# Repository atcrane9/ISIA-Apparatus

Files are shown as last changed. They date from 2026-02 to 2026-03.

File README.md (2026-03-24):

# ISIA-Apparatus

The "Immersive Social Interactions Assay" (ISIA) apparatus is a modular system designed to connect multiple mouse cages together, while allowing the option to restrict certain mice to specific cages.

The link to Methods Paper for this apparatus can be found [here]()

## Hardware

All files were printed using a Prusa i3 MKS3, using OVERTURE PLA Plus (PLA+) 1.75mm Professional Toughness filament.\
Painter's tape was put on print bed to increase print adhesion with bed.
* Make sure tape is completely flat
* No gaps between tape pieces
* If tape tears when removing print, replace with new piece
  
Nozzles used were either 0.4mm or 0.6mm, depending on specific part (Instructions for changing the nozzles [here](https://help.prusa3d.com/article/changing-or-replacing-the-nozzle-mk2-5-s-mk3-s-mk3-5-s_2069))
* **<ins>Must</ins>** be printed using **<ins>0.4mm nozzle</ins>**
  * [Cap](STL_Files/ISIA_Cap.stl)
  * [Adapter](STL_Files/ISIA_Adapter.stl)
  * [Inner Gate](STL_Files/ISIA_Inner_Gate.stl)
  * [Outer Gate](STL_Files/ISIA_Outer_Gate.stl)

_Note: These 4 parts contain threads that allow them to screw together. However, the threads must be "broken in" after printing, which is done by repeatedly screwing/unscrewing the parts with each other until they can easily twist the full range with minimal friction._

* Can be printed using **<ins>0.6mm nozzle</ins>**
  * [Tube](STL_Files/ISIA_Tube.stl)
  * [Restrictor](STL_Files/ISIA_Restrictor.stl)

### Cleaning
To clean the ISIA parts for reuse between experiments, scrub all surfaces vigorously using a sponge and dish soap.
* For the Tube, instead put dish soap on a toothbrush and scrub the inside and outside surfaces vigorously

_Note: While all other parts are reusable between experiments after cleaning, the Restictors are not resuasble, as the restricted mice often slightly chew on them in an attempt to reach the other cage. We advise printing new Restrictors for each experiment, and disposing of them when the experiment ends._

## Software

All parts sliced (aka rendered) using PrusaSlicer 2.9.2

Full print settings found here:\
[0.4mm nozzle settings](PrinterSettings/0.4nozzle_settings_no_support.ini)\
[0.6mm nozzle settings](PrinterSettings/0.6nozzle_settings_no_support.ini)

### Key Settings
* No skirt, no brim, no support material, no raft 
* First layer speed: 10mm/s 
* First layer height: 0.2mm 
* Infill density: 5%
* Layer Height:
  * For **<ins>0.4mm</ins>** Nozzle -> 0.3mm layer height
  * For **<ins>0.6mm</ins>** Nozzle -> 0.4mm layer height

# ISIA Apparatus Construction
_Note: See [Methods Paper]() for guide on how to modify mouse cages to work with this system_
1. Place Inner Gate on the inside of ISIA cage bottom, with the threads poking through the 51mm cage hole
   <p>
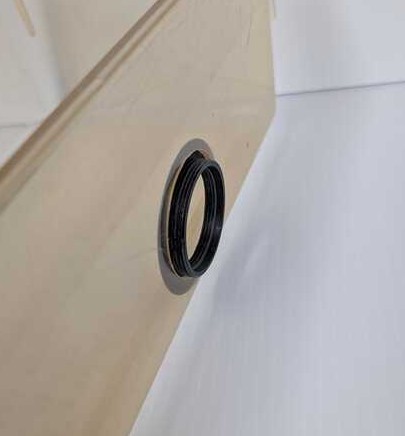
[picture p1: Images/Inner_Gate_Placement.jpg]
    
   </p>
2. Screw Outer Gate onto the threads of the Inner Gate
   * There are small ridges outside of the Outer Gates that go up ~3/4 of the height, leaving a small gap. This gap indicates the top of the Outer Gate, which is the side that screws onto the Inner Gate
   <p>
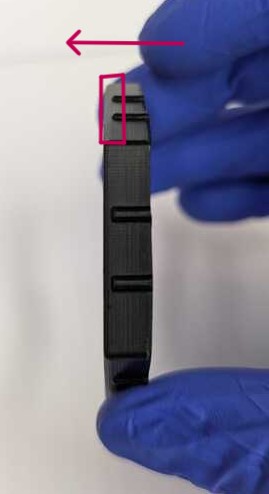
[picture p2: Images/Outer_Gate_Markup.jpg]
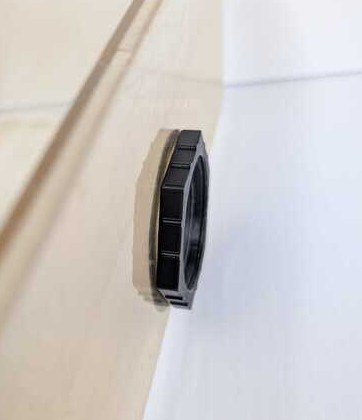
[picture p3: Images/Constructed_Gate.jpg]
     
   </p>
4. Repeat for both 51mm diameter cage holes

### To Close Gate:
* Screw Cap into Gate
  <p>
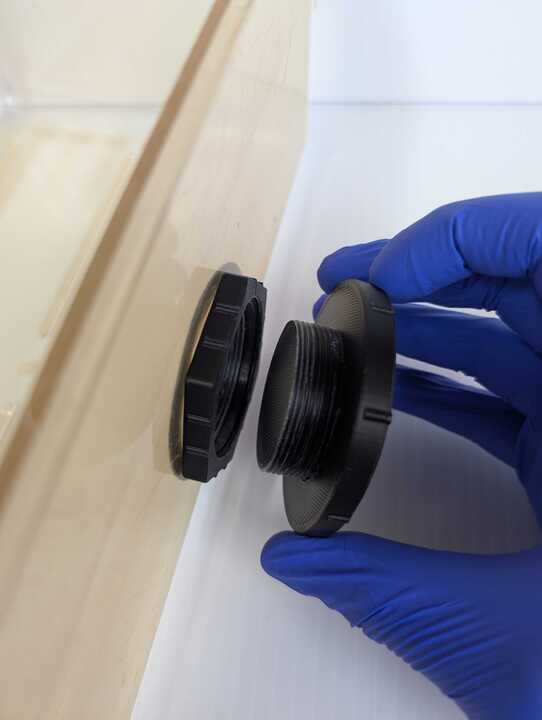
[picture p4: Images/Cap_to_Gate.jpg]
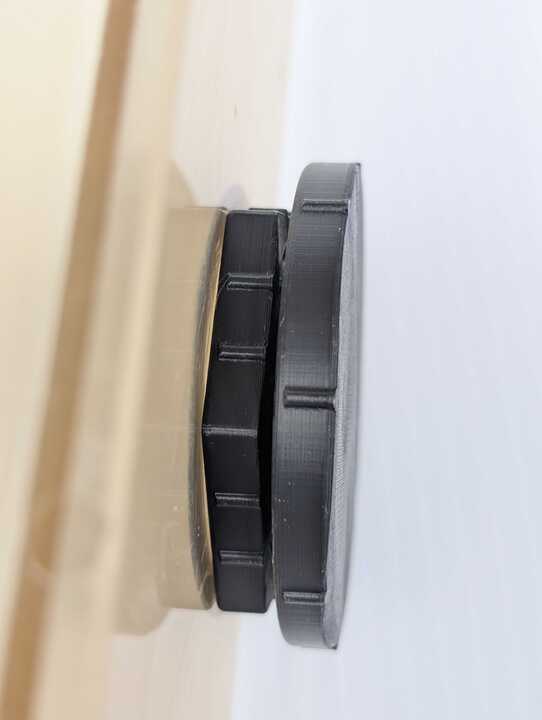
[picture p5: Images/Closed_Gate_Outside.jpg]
     
   </p>
  Should look like this from inside:
   <p>
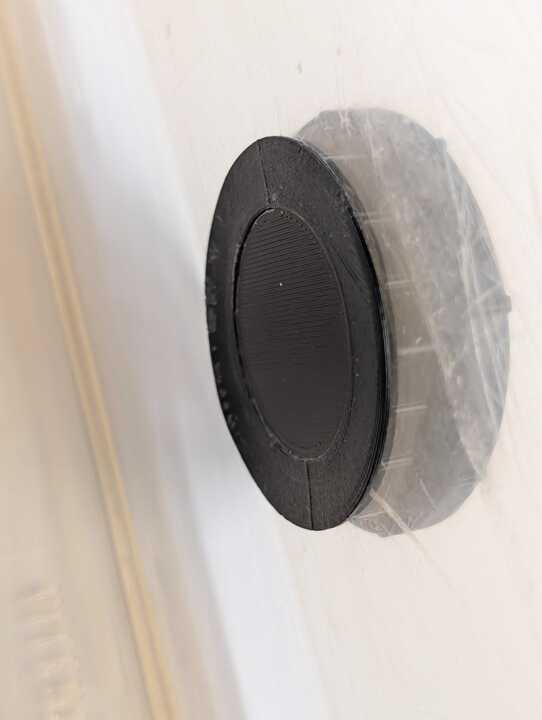
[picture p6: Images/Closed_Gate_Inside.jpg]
    
   </p>

### To Connect Gate to Tube:
* Screw Adapter into Gate
   <p>
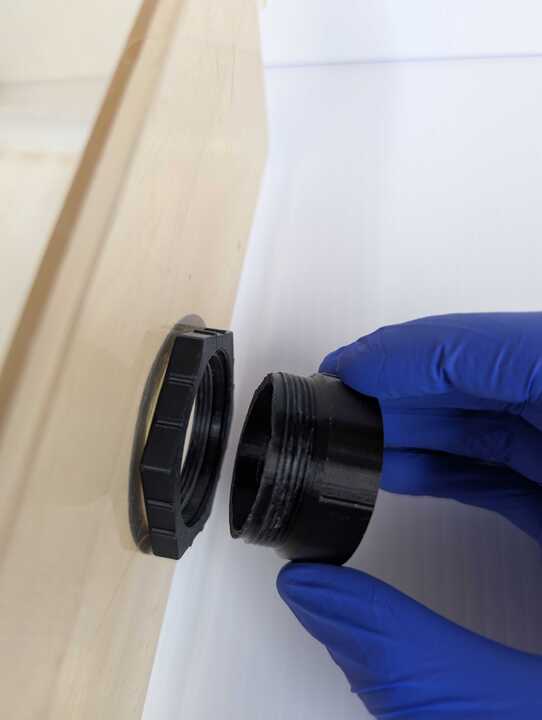
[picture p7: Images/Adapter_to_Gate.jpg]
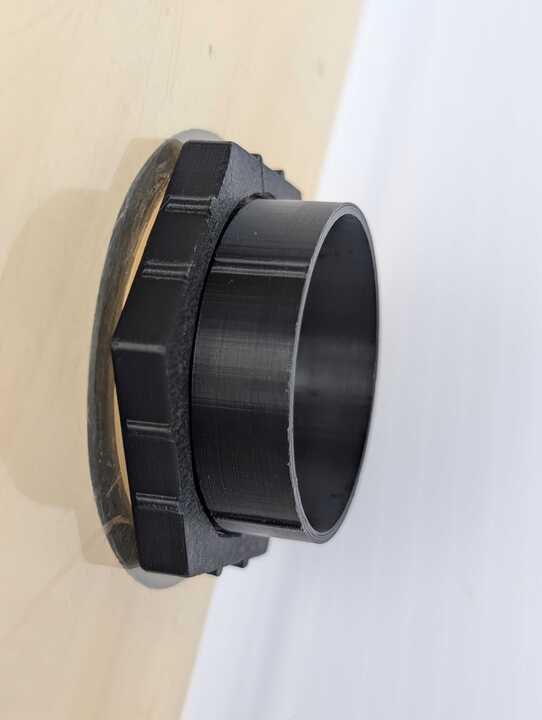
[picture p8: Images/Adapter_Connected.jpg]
     
   </p>
* Connect Tube to Adapter
  * _Note: The tube and adapter slide together, there is no screw with this connection_
  <p>
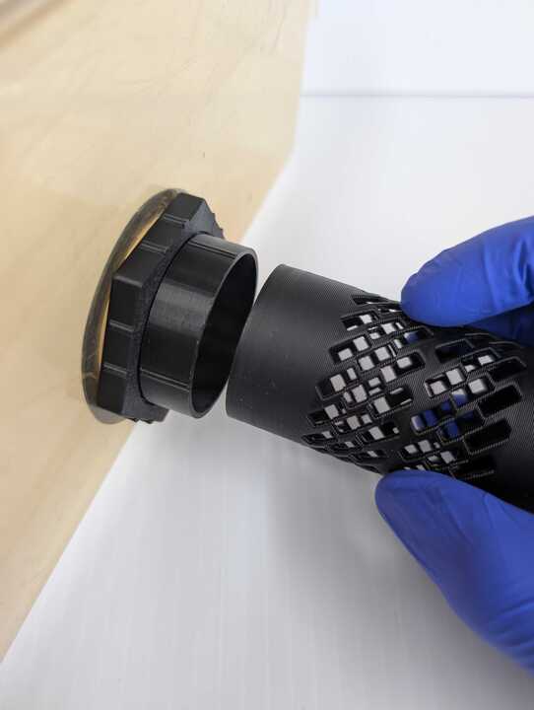
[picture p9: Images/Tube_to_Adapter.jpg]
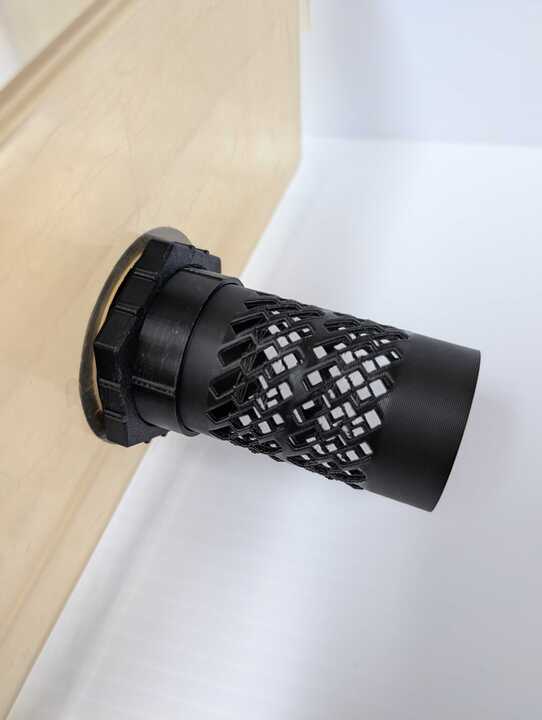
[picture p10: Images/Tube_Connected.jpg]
     
   </p>
* Connect second ISIA cage to other end of Tube
  * Make sure that water bottle holes are both facing the same direction
    * If they are opposite, swap the Cap and Adapter on one of the cages
  * Make sure to firmly push cages together to prevent tube from falling out
### To Restrict Mice
1. Separate cage containing restricted mouse from the tube
   <!-- * Can temporarily block open Gate with a Cap to prevent mice from escaping
     _Note that the Cap does not fit tightly into the Adapter, it is possible ????_
   <p>
    <img src=Images/Cap_to_Adapter.jpg height="290"> <img src=Images/Cap_block_Adapter.jpg height="290">
   </p> -->
2. Add Restrictor to exposed Tube entrance
   <p>
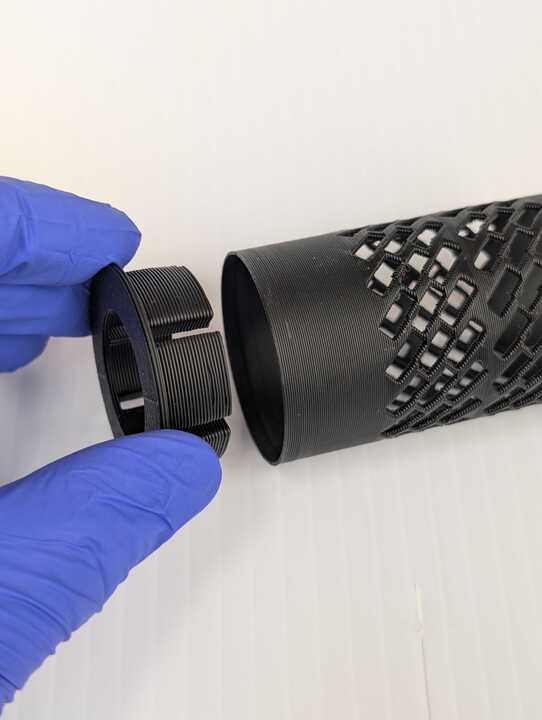
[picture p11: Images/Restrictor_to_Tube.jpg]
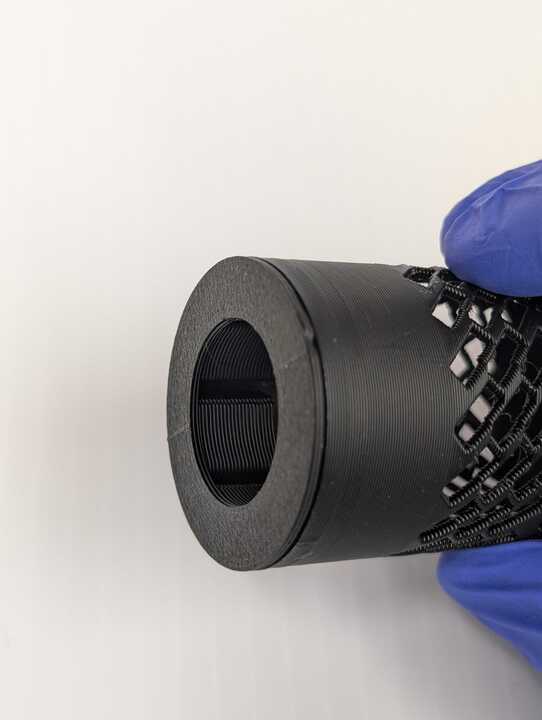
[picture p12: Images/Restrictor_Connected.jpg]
     
   </p>
3. Reconnect Tube to Adapter
   <p>
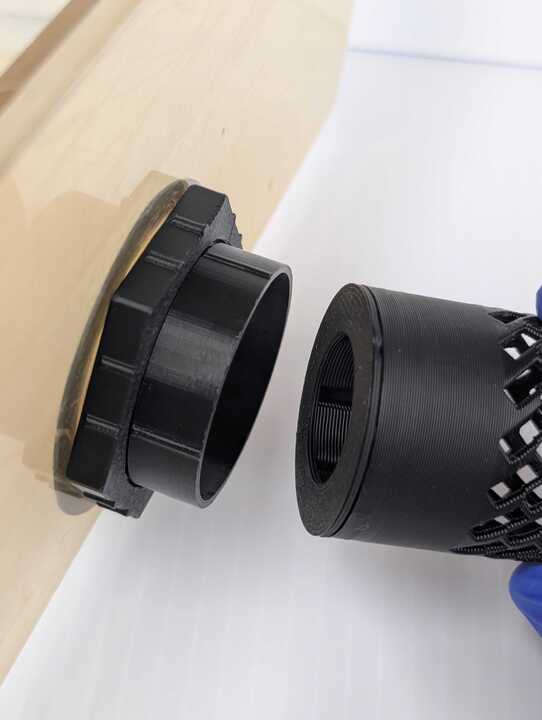
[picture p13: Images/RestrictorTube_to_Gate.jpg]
     
   </p>
   Should look like this from inside:<br/>
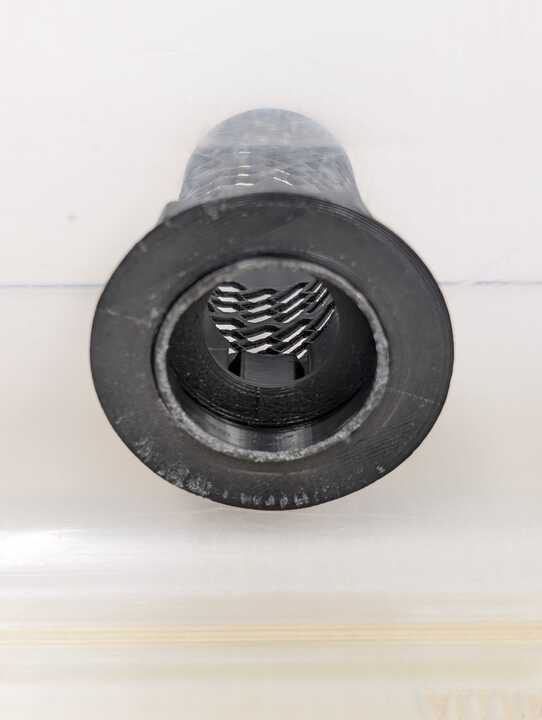
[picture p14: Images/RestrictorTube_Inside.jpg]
   

## Completed Setup looks like this:
   <p>
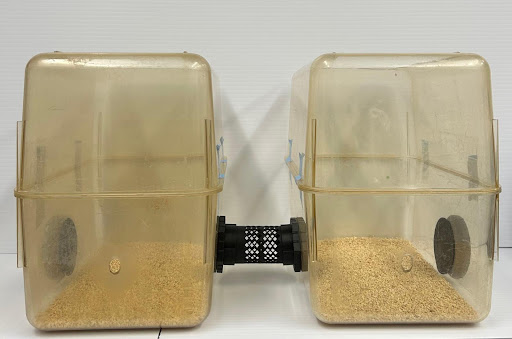
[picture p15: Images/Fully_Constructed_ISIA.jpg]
    
   </p>

# Acknowledgments

* [Aaron Crane](https://github.com/atcrane9) - Original designs for the Cap, Adapter, Inner and Outer Gates, updates to the Tube design, and compatibility of entire ensamble
* [The AER Lab](https://github.com/AER-Lab)
* [Matt Gaidica](https://github.com/mattgaidica) - First iteration design of Tube, Restrictor (Insert), and Flange

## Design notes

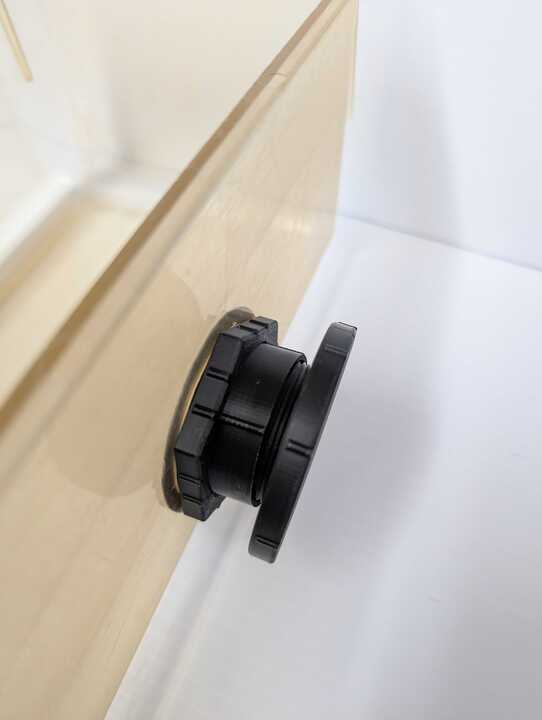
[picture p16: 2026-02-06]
Images/Cap_block_Adapter.jpg

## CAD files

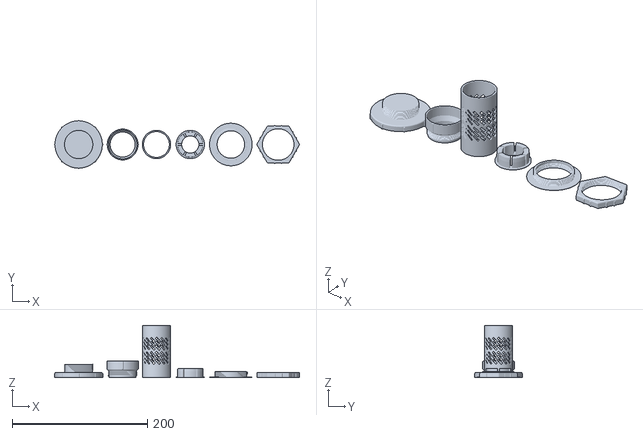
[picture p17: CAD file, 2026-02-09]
STL_Files/ISIA_Ensamble.stl
362.2 x 71.5 x 77.6

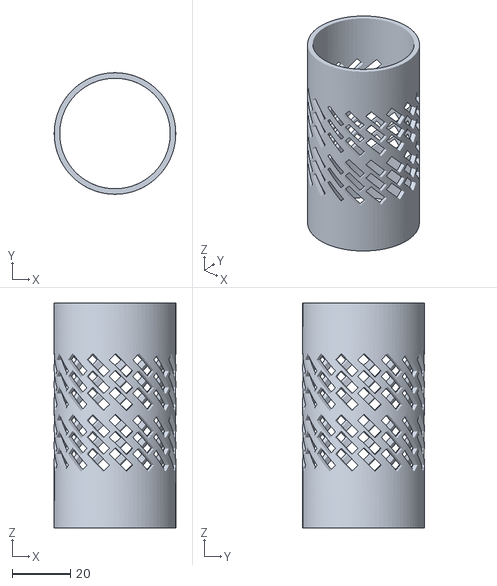
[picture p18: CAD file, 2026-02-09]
STL_Files/ISIA_Tube.stl
41.9 x 41.9 x 77.6

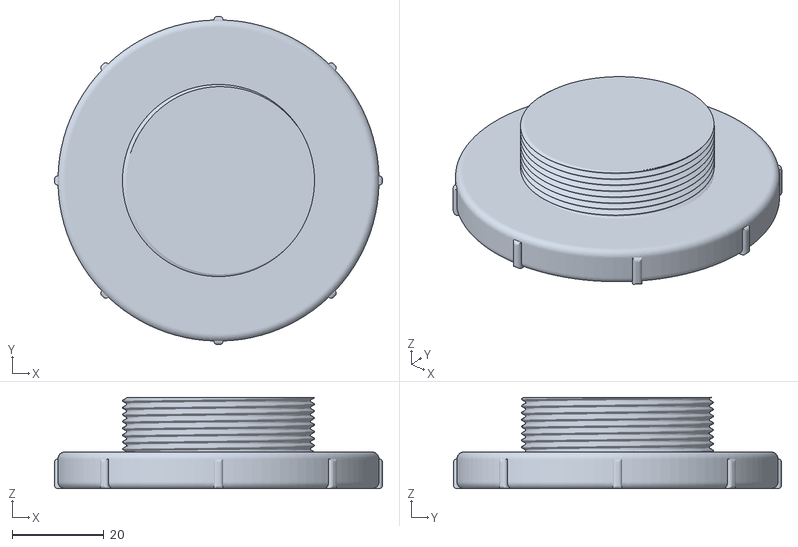
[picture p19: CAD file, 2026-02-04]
STL_Files/ISIA_Cap.stl
71.5 x 71.5 x 19.9

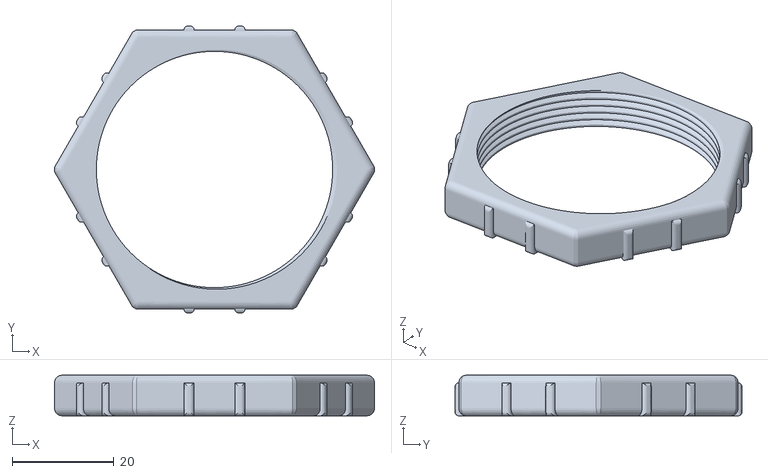
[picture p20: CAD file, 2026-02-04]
STL_Files/ISIA_Outer_Gate.stl
63.0 x 56.5 x 8.00

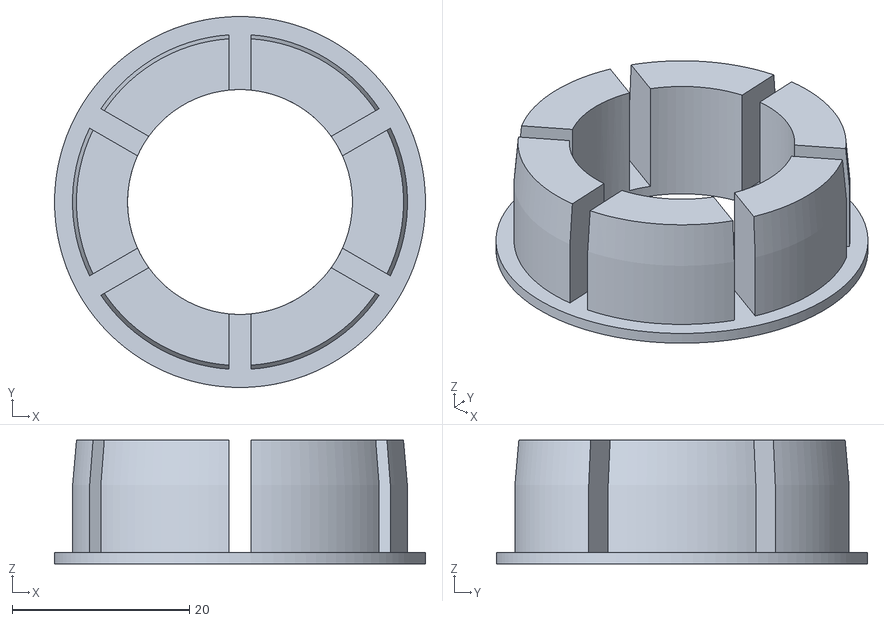
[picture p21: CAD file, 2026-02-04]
STL_Files/ISIA_Restrictor.stl
41.9 x 41.9 x 14.0

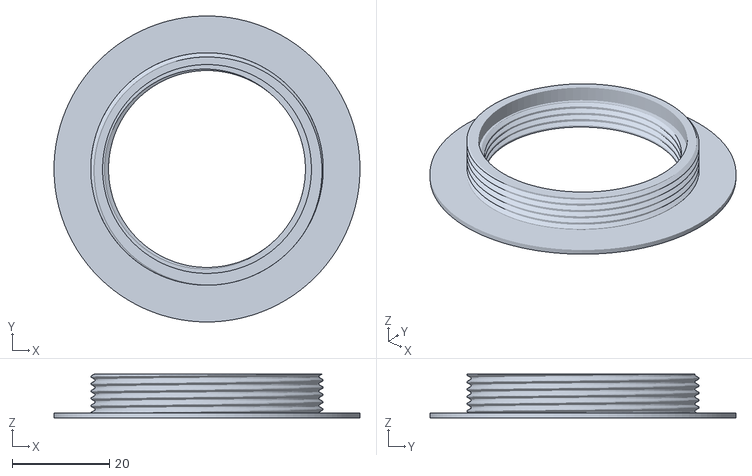
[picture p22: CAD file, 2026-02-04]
STL_Files/ISIA_Inner_Gate.stl
63.0 x 63.0 x 9.00

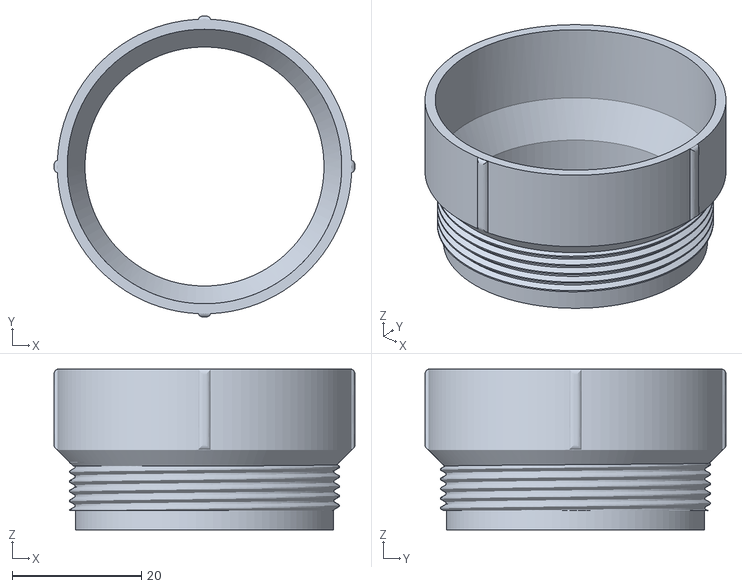
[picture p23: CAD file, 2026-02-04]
STL_Files/ISIA_Adapter.stl
46.6 x 46.6 x 24.9

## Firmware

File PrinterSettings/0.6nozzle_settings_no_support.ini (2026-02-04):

# generated by PrusaSlicer 2.9.2 on 2025-10-06 at 19:56:54 UTC
arc_fitting = disabled
autoemit_temperature_commands = 1
automatic_extrusion_widths = 0
automatic_infill_combination = 0
automatic_infill_combination_max_layer_height = 100%
avoid_crossing_curled_overhangs = 0
avoid_crossing_perimeters = 0
avoid_crossing_perimeters_max_detour = 0
bed_custom_model = 
bed_custom_texture = 
bed_shape = 0x0,250x0,250x210,0x210
bed_temperature = 0
bed_temperature_extruder = 0
before_layer_gcode = ;BEFORE_LAYER_CHANGE\nG92 E0.0\n;[layer_z]\n\n
between_objects_gcode = 
binary_gcode = 0
bottom_fill_pattern = monotonic
bottom_solid_layers = 3
bottom_solid_min_thickness = 0.6
bridge_acceleration = 1000
bridge_angle = 0
bridge_fan_speed = 100
bridge_flow_ratio = 0.95
bridge_speed = 25
brim_separation = 0
brim_type = no_brim
brim_width = 0
chamber_minimal_temperature = 0
chamber_temperature = 0
color_change_gcode = M600\nG1 E0.5 F1500 ; prime after color change
colorprint_heights = 
compatible_printers_condition_cummulative = "printer_notes=~/.*PRINTER_VENDOR_PRUSA3D.*/ and printer_notes=~/.*PRINTER_MODEL_MK3.*/ and nozzle_diameter[0]==0.6";
complete_objects = 0
cooling = 1
cooling_tube_length = 5
cooling_tube_retraction = 91.5
default_acceleration = 1000
default_filament_profile = "Prusament PLA"
default_print_profile = 0.30mm QUALITY @0.6 nozzle MK3
deretract_speed = 25
disable_fan_first_layers = 3
dont_support_bridges = 0
draft_shield = disabled
duplicate_distance = 6
elefant_foot_compensation = 0.2
enable_dynamic_fan_speeds = 0
enable_dynamic_overhang_speeds = 0
end_filament_gcode = "; Filament-specific end gcode \n;END gcode for filament\n"
end_gcode = {if max_layer_z < max_print_height}G1 Z{z_offset+min(max_layer_z+1, max_print_height)} F720 ; Move print head up{endif}\nG1 X0 Y200 F3600 ; park\n{if max_layer_z < max_print_height}G1 Z{z_offset+min(max_layer_z+49, max_print_height)} F720 ; Move print head further up{endif}\nG4 ; wait\nM221 S100 ; reset flow\nM900 K0 ; reset LA\n{if print_settings_id=~/.*(DETAIL @MK3|QUALITY @MK3|@0.25 nozzle MK3).*/}M907 E538 ; reset extruder motor current{endif}\nM104 S0 ; turn off temperature\nM140 S0 ; turn off heatbed\nM107 ; turn off fan\nM84 ; disable motors\n; max_layer_z = [max_layer_z]
ensure_vertical_shell_thickness = enabled
external_perimeter_acceleration = 0
external_perimeter_extrusion_width = 0.68
external_perimeter_speed = 30
external_perimeters_first = 0
extra_loading_move = -2
extra_perimeters = 0
extra_perimeters_on_overhangs = 0
extruder_clearance_height = 20
extruder_clearance_radius = 45
extruder_colour = ""
extruder_offset = 0x0
extrusion_axis = E
extrusion_multiplier = 1
extrusion_width = 0.65
fan_always_on = 0
fan_below_layer_time = 60
filament_abrasive = 0
filament_colour = #29B2B2
filament_cooling_final_speed = 3.4
filament_cooling_initial_speed = 2.2
filament_cooling_moves = 4
filament_cost = 0
filament_density = 0
filament_deretract_speed = nil
filament_diameter = 1.75
filament_infill_max_crossing_speed = 0
filament_infill_max_speed = 0
filament_load_time = 0
filament_loading_speed = 28
filament_loading_speed_start = 3
filament_max_volumetric_speed = 0
filament_minimal_purge_on_wipe_tower = 15
filament_multitool_ramming = 0
filament_multitool_ramming_flow = 10
filament_multitool_ramming_volume = 10
filament_notes = ""
filament_purge_multiplier = 100%
filament_ramming_parameters = "120 100 6.6 6.8 7.2 7.6 7.9 8.2 8.7 9.4 9.9 10.0| 0.05 6.6 0.45 6.8 0.95 7.8 1.45 8.3 1.95 9.7 2.45 10 2.95 7.6 3.45 7.6 3.95 7.6 4.45 7.6 4.95 7.6"
filament_retract_before_travel = nil
filament_retract_before_wipe = nil
filament_retract_layer_change = nil
filament_retract_length = nil
filament_retract_length_toolchange = nil
filament_retract_lift = nil
filament_retract_lift_above = nil
filament_retract_lift_below = nil
filament_retract_restart_extra = nil
filament_retract_restart_extra_toolchange = nil
filament_retract_speed = nil
filament_seam_gap_distance = nil
filament_settings_id = "- default -"
filament_shrinkage_compensation_xy = 0%
filament_shrinkage_compensation_z = 0%
filament_soluble = 0
filament_spool_weight = 0
filament_stamping_distance = 0
filament_stamping_loading_speed = 20
filament_toolchange_delay = 0
filament_travel_lift_before_obstacle = nil
filament_travel_max_lift = nil
filament_travel_ramping_lift = nil
filament_travel_slope = nil
filament_type = PLA
filament_unload_time = 0
filament_unloading_speed = 90
filament_unloading_speed_start = 100
filament_vendor = (Unknown)
filament_wipe = nil
fill_angle = 45
fill_density = 5%
fill_pattern = gyroid
first_layer_acceleration = 800
first_layer_acceleration_over_raft = 0
first_layer_bed_temperature = 0
first_layer_extrusion_width = 0.65
first_layer_height = 0.2
first_layer_infill_speed = 0
first_layer_speed = 10
first_layer_speed_over_raft = 30
first_layer_temperature = 200
full_fan_speed_layer = 0
fuzzy_skin = none
fuzzy_skin_point_dist = 0.8
fuzzy_skin_thickness = 0.3
gap_fill_enabled = 1
gap_fill_speed = 35
gcode_comments = 0
gcode_flavor = marlin
gcode_label_objects = octoprint
gcode_resolution = 0.0125
gcode_substitutions = 
high_current_on_filament_swap = 0
host_type = octoprint
idle_temperature = nil
infill_acceleration = 1000
infill_anchor = 2.5
infill_anchor_max = 15
infill_every_layers = 1
infill_extruder = 1
infill_extrusion_width = 0.68
infill_first = 0
infill_overlap = 15%
infill_speed = 45
inherits_cummulative = "0.40mm DRAFT @0.6 nozzle MK3";;"Original Prusa i3 MK3S & MK3S+ 0.6 nozzle"
interface_shells = 0
interlocking_beam = 0
interlocking_beam_layer_count = 2
interlocking_beam_width = 0.8
interlocking_boundary_avoidance = 2
interlocking_depth = 2
interlocking_orientation = 22.5
ironing = 0
ironing_flowrate = 15%
ironing_spacing = 0.1
ironing_speed = 15
ironing_type = top
layer_gcode = ;AFTER_LAYER_CHANGE\n;[layer_z]
layer_height = 0.4
machine_limits_usage = emit_to_gcode
machine_max_acceleration_e = 5000,5000
machine_max_acceleration_extruding = 1250,1250
machine_max_acceleration_retracting = 1250,1250
machine_max_acceleration_travel = 1500,1250
machine_max_acceleration_x = 1000,960
machine_max_acceleration_y = 1000,960
machine_max_acceleration_z = 200,200
machine_max_feedrate_e = 120,120
machine_max_feedrate_x = 200,100
machine_max_feedrate_y = 200,100
machine_max_feedrate_z = 12,12
machine_max_jerk_e = 4.5,4.5
machine_max_jerk_x = 8,8
machine_max_jerk_y = 8,8
machine_max_jerk_z = 0.4,0.4
machine_min_extruding_rate = 0,0
machine_min_travel_rate = 0,0
max_fan_speed = 100
max_layer_height = 0.4
max_print_height = 210
max_print_speed = 100
max_volumetric_extrusion_rate_slope_negative = 0
max_volumetric_extrusion_rate_slope_positive = 0
max_volumetric_speed = 0
min_bead_width = 85%
min_fan_speed = 35
min_feature_size = 25%
min_layer_height = 0.15
min_print_speed = 10
min_skirt_length = 4
mmu_segmented_region_interlocking_depth = 0
mmu_segmented_region_max_width = 0
multimaterial_purging = 140
notes = 
nozzle_diameter = 0.6
nozzle_high_flow = 0
only_one_perimeter_first_layer = 0
only_retract_when_crossing_perimeters = 0
ooze_prevention = 0
output_filename_format = {input_filename_base}_{nozzle_diameter[0]}n_{layer_height}mm_{printing_filament_types}_{printer_model}_{print_time}.gcode
over_bridge_speed = 0
overhang_fan_speed_0 = 0
overhang_fan_speed_1 = 0
overhang_fan_speed_2 = 0
overhang_fan_speed_3 = 0
overhang_speed_0 = 15
overhang_speed_1 = 15
overhang_speed_2 = 20
overhang_speed_3 = 25
overhangs = 1
parking_pos_retraction = 92
pause_print_gcode = M601
perimeter_acceleration = 800
perimeter_extruder = 1
perimeter_extrusion_width = 0.68
perimeter_generator = arachne
perimeter_speed = 35
perimeters = 2
physical_printer_settings_id = 
post_process = 
prefer_clockwise_movements = 0
print_host = 
print_settings_id = 0.6_nozzle_MK3_slow_Infill_0.6_Layer_no_sup
printer_model = MK3S
printer_notes = Don't remove the following keywords! These keywords are used in the "compatible printer" condition of the print and filament profiles to link the particular print and filament profiles to this printer profile.\nPRINTER_VENDOR_PRUSA3D\nPRINTER_MODEL_MK3\n
printer_settings_id = Original Prusa i3 MK3S & MK3S+ 0.6 nozzle
printer_technology = FFF
printer_variant = 0.6
printer_vendor = 
printhost_apikey = 
printhost_cafile = 
raft_contact_distance = 0.25
raft_expansion = 1.5
raft_first_layer_density = 90%
raft_first_layer_expansion = 3
raft_layers = 0
remaining_times = 1
resolution = 0
retract_before_travel = 1
retract_before_wipe = 0%
retract_layer_change = 1
retract_length = 0.8
retract_length_toolchange = 4
retract_lift = 0.4
retract_lift_above = 0
retract_lift_below = 209
retract_restart_extra = 0
retract_restart_extra_toolchange = 0
retract_speed = 35
scarf_seam_entire_loop = 0
scarf_seam_length = 20
scarf_seam_max_segment_length = 1
scarf_seam_on_inner_perimeters = 0
scarf_seam_only_on_smooth = 1
scarf_seam_placement = nowhere
scarf_seam_start_height = 0%
seam_gap_distance = 15%
seam_position = aligned
silent_mode = 1
single_extruder_multi_material = 0
single_extruder_multi_material_priming = 0
skirt_distance = 2
skirt_height = 3
skirts = 0
slice_closing_radius = 0.049
slicing_mode = regular
slowdown_below_layer_time = 5
small_perimeter_speed = 20
solid_infill_acceleration = 0
solid_infill_below_area = 0
solid_infill_every_layers = 0
solid_infill_extruder = 1
solid_infill_extrusion_width = 0.68
solid_infill_speed = 45
spiral_vase = 0
staggered_inner_seams = 0
standby_temperature_delta = -5
start_filament_gcode = "; Filament gcode\n"
start_gcode = M862.3 P "[printer_model]" ; printer model check\nM862.1 P[nozzle_diameter] ; nozzle diameter check\nM115 U3.12.2 ; tell printer latest fw version\nG90 ; use absolute coordinates\nM83 ; extruder relative mode\nM104 S[first_layer_temperature] ; set extruder temp\nM140 S[first_layer_bed_temperature] ; set bed temp\nM190 S[first_layer_bed_temperature] ; wait for bed temp\nM109 S[first_layer_temperature] ; wait for extruder temp\nG28 W ; home all without mesh bed level\nG80 ; mesh bed leveling\n{if filament_settings_id[initial_tool]=~/.*Prusament PA11.*/}\nG1 Z0.3 F720\nG1 Y-3 F1000 ; go outside print area\nG92 E0\nG1 X60 E9 F1000 ; intro line\nG1 X100 E9 F1000 ; intro line\n{else}\nG1 Z0.2 F720\nG1 Y-3 F1000 ; go outside print area\nG92 E0\nG1 X60 E9 F1000 ; intro line\nG1 X100 E12.5 F1000 ; intro line\n{endif}\nG92 E0\nM221 S{if layer_height<0.075}100{else}95{endif}
support_material = 0
support_material_angle = 0
support_material_auto = 1
support_material_bottom_contact_distance = 0
support_material_bottom_interface_layers = -1
support_material_buildplate_only = 0
support_material_closing_radius = 2
support_material_contact_distance = 0.3
support_material_enforce_layers = 0
support_material_extruder = 0
support_material_extrusion_width = 0.61
support_material_interface_contact_loops = 0
support_material_interface_extruder = 0
support_material_interface_layers = 2
support_material_interface_pattern = concentric
support_material_interface_spacing = 0.5
support_material_interface_speed = 80%
support_material_pattern = honeycomb
support_material_spacing = 2
support_material_speed = 50
support_material_style = grid
support_material_synchronize_layers = 0
support_material_threshold = 50
support_material_with_sheath = 0
support_material_xy_spacing = 90%
support_tree_angle = 40
support_tree_angle_slow = 25
support_tree_branch_diameter = 2
support_tree_branch_diameter_angle = 5
support_tree_branch_diameter_double_wall = 3
support_tree_branch_distance = 1
support_tree_tip_diameter = 0.8
support_tree_top_rate = 15%
temperature = 200
template_custom_gcode = 
thick_bridges = 0
thin_walls = 0
thumbnails = 160x120/PNG
thumbnails_format = PNG
toolchange_gcode = 
top_fill_pattern = monotoniclines
top_infill_extrusion_width = 0.65
top_one_perimeter_type = none
top_solid_infill_acceleration = 0
top_solid_infill_speed = 35
top_solid_layers = 4
top_solid_min_thickness = 0.9
travel_acceleration = 0
travel_lift_before_obstacle = 0
travel_max_lift = 0
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

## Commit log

2026-02-04 Create PrinterSettings Folder
2026-02-04 Update and rename 0.4nozzle_settings_no_support.ini to PrinterSettings/0.4nozzle_settings_no_support.ini
2026-02-04 Update and rename 0.6nozzle_settings_no_support.ini to PrinterSettings/0.6nozzle_settings_no_support.ini
